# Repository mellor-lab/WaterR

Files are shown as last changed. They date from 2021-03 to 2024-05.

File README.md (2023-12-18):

# WaterR

WaterR is an open-source device developed in the Dodson lab at the University of Bristol to automate fluid restriction in experimental rodents. It allows the user to: set water-availability time windows, set a maximum daily volume allowance, or deliver ad libitum water to assess baseline water consumption. Automating water access-control offers the opportunity to significantly refine current practice. The ability to monitor water consumption on a cage-by-cage basis and the flexibility offered in programming different water-access regimens allows the implementation of tailored restriction approaches, while at the same time offering a standardised platform to aid reproducibility across different laboratories. 
<p align="center">
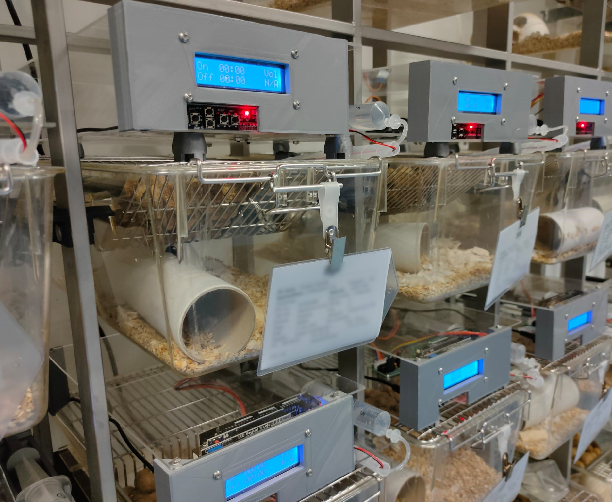
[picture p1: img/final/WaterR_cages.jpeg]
    
</p>
&nbsp;

## List of components
In the table below there is a list of all components necessary to assemble WaterR. A source for each component is added for ease but every component is readily available from other sources as well. Links or part numbers are added for ease; part numbers are provided as manufacturer numbers instead of supplier as it makes it easier to source the items from a different supplier should you need to do so. Multi-buy options are provided when possible as they are cheaper, the quantity required for a single WaterR unit is listed in the table.  
Note: it is important that the power supply is a grounded, desktop power supply (i.e. a "brick") with a low ripple current (<100 mV peak-to-peak), otherwise it could interfere with the signal from the piezoelectric vibration sensor. These can be quite expensive (£40-50 each) but they provide up to 6-8 Amps, and as 1 WaterR unit uses ~500 mA you can safely power multiple units from one supply. Refrain from using a cheap switching power supply!

| Component                         | Source            | Catalog num / reference | Q.ty for 1 unit    |
|-----------------------------------|-------------------|-------------------------|--------------------|
| **Main items**                    |                   |                         |                    |
| ELEGOO Mega 2560                  | Amazon            | https://amzn.to/380VEm9 | 1                  |
| LCD keypad shield                 | Amazon            | https://amzn.to/3uISKfw | 1                  |
| Data Logging shield with RTC      | Amazon            | https://amzn.to/3ra0zZz | 1                  |
| Stepper Motor 28byj-48, 5V, 1:64  | Amazon            | https://amzn.to/2NCnqOH | 1                  |
| A4 acrylic sheet, 2mm             | Amazon            | https://amzn.to/2Ps0bYr | 2                  |
| Terumo 20ml syringe               | Medline Scientific| BS-20ES                 | 1                  |
| **Spout block**                   |                   |                         |                    |
| Piezoelectric sensor              | RS components     | 285-784                 | 1                  |
| Hook up wire, red                 | RS components     | 872-4460                | 30 cm              |
| Hook up wire, black               | RS components     | 872-4458                | 30 cm              |
| Resistor, 10 MΩ                   | Farnell           | RE03841                 | 1                  |
| Heath-shrink tubing               | Amazon            | https://amzn.to/3uOrmwP | various sizes      |
| 2.54 mm pin header , 2x1          | RS components     | 251-8086                | 1                  |
| Spiral Wrap                       | RS components     | 227-980                 | 15 cm              |
| Fitting, female luer to 1/16 barb | Cole-Parmer       | 45508-00                | 1                  |
| Fitting, male luer to 1/16 barb   | Cole-Parmer       | 45505-22                | 1                  |
| Tygon tubing, 1.6 ID x 3.2mm OD   | Cole-Parmer       | ACF00002                | 20 cm              |
| Surflo cathether 16Gx51mm         | VWR International | SR+OX1651C1             | 1                  |
| **Power**                         |                   |                         |                    |
| DC power splitter, 5 way          | Farnell           | C-PS-5W                 | 1 shared among 5   |
| DC power extensions, 1M           | Farnell           | PSG02089                | 1                  |
| Power supply, 9V, 4.5A            | RS components     | 175-9086                | 1 shared among 6-8 |
| **Fasteners**                     |                   |                         |                    |
| Screw, M3 x 20mm                  | Technobots        | 4304-320                | 4                  |
| Screw, M3 x 8mm                   | Technobots        | 4304-308                | 2                  |
| Screw, M3 x 6mm                   | Technobots        | 4304-306                | 14                 |
| Screw, M3 x 8mm, countersunk      | Technobots        | 4304-408                | 2                  |
| Nut, M3                           | Technobots        | 4310-025                | 6                  |
| Zip ties, 250mm	            | Amazon            | https://amz.run/5GKi    | 1                  |
| Dupont wires, 10cm                | Amazon            | https://amzn.to/3834WxT | 6 (f-m), 1 (m-m)   |
| CR1225 lithium battery            | Farnell           | CR1225                  | 1 (or 0)           |

## Tools
M3 Hex screwdriver (2mm)  
M3 Hex nut driver (5.5mm)  
Electric drill (4mm drill bit)  
Dremel  
Soldering iron  
Wire cutter

## 3D printed parts
You should print all the files in the /stl_parts folder. FDM printers are better suited for this job as it doesn’t require laser precision and it’s faster. Everything except for the Pump_motor_pinion.stl and the Spout_cover.stl can be printed at 0.15mm layer size, the former should be printed at least at 0.1mm or 0.06mm. Pump_rack should be printed sideways to avoid having weak line spots at the top of the teeth.

## Controller block
Take the keypad shield and cut the pin that would connect to pin 10 of the Arduino as shown in figure (this is to avoid conflicts with the clock/sd shield). 
<p align="center">
    
</p>
&nbsp; 

Take a male-male dupont cable and cut it in half. Solder the cut extremities onto the clock/sd shield, in the holes labelled SDA and SCL on the board (as shown in image). Sometimes the shield comes with 2.54 mm header soldered in this position, in this case just solder the wires to the corresponding header pins.
Add the CR1225 button battery in the clock/sd shield if it came without one. If it came with one you can still swap in a fresh one as these shields can sit on a shelf for years, affecting the amount of charge left in the battery.
<p align="center">
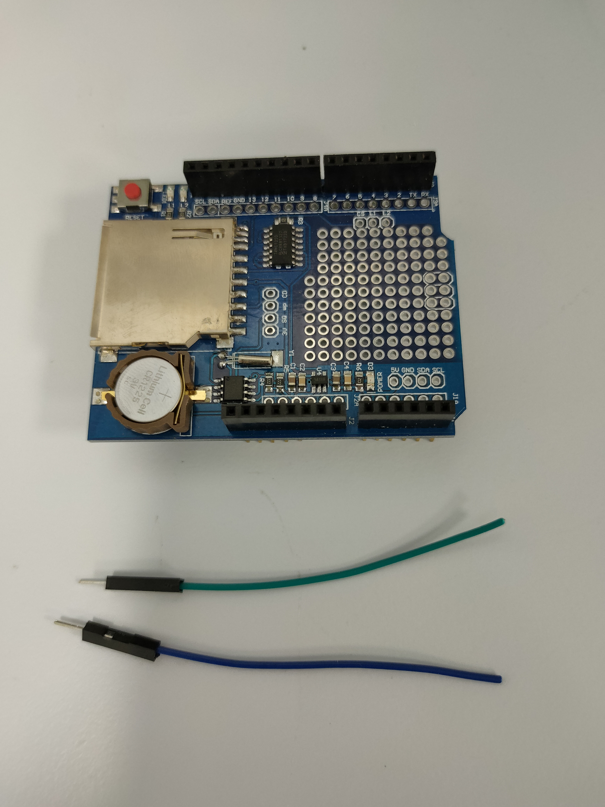
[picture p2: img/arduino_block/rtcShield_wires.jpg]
    
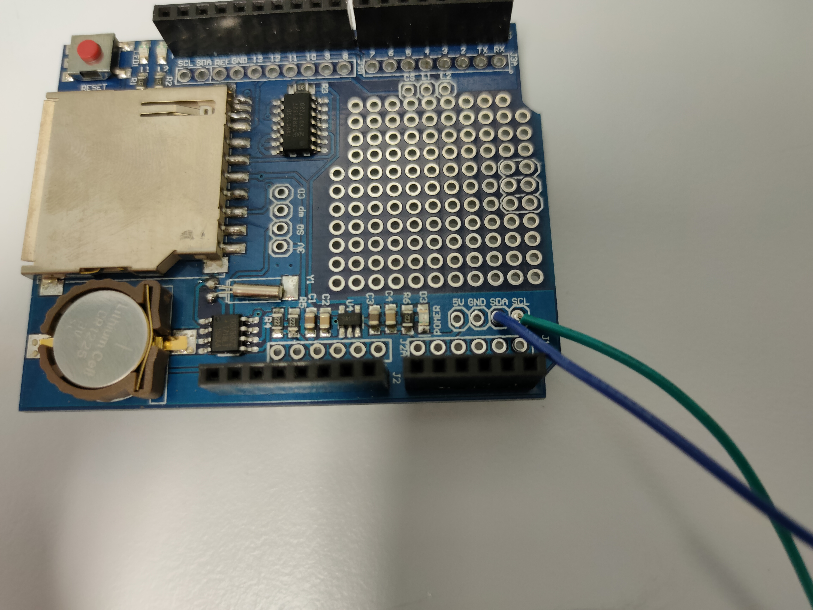
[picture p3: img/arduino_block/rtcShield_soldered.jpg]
    
</p>
&nbsp;

Slot the clock/sd shield onto the Arduino and connect the SDA wire on the SDA pin (pin 20) on the Arduino and do the same with clock/sd shield SCL and Arduino SCL (pin 21). Slot the LCD keypad shield on top of the clock/sd shield.
<p align="center">
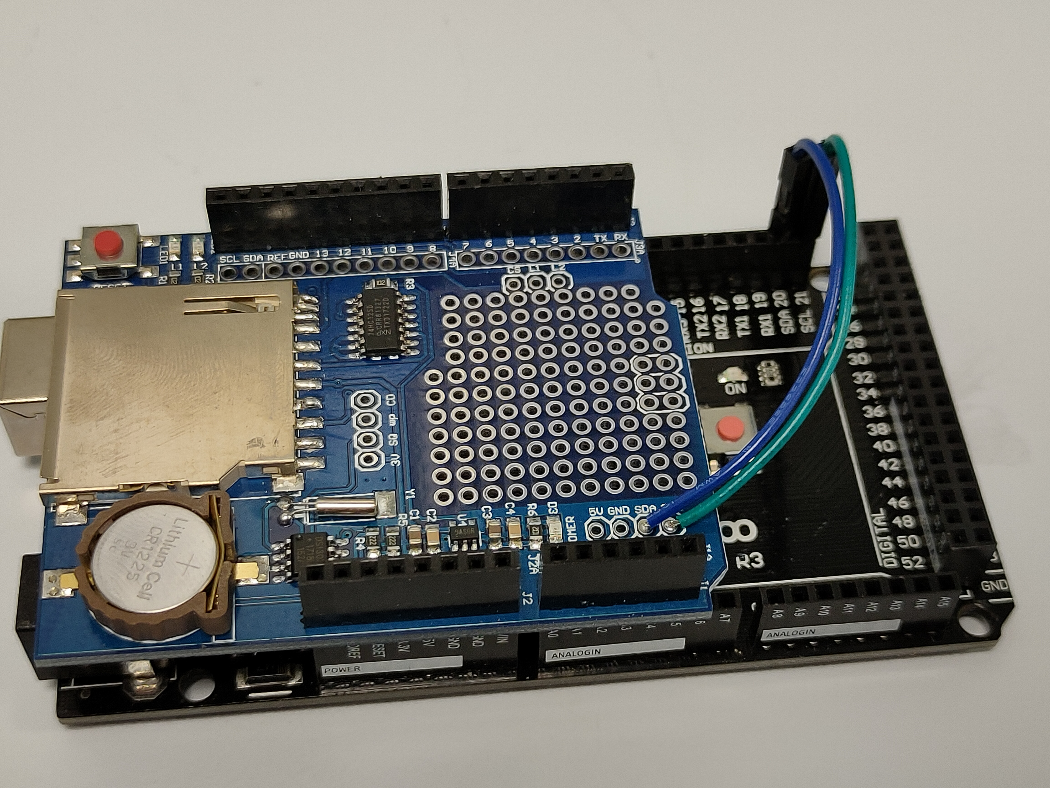
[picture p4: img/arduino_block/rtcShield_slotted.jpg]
    
</p>
&nbsp;

Now we can upload the software required to sync the clock and the WaterR firmware.

## Software
1. Install the [Arduino IDE](https://www.arduino.cc/en/software) if you have not done so already.

2. Download the WaterR repository to your computer.

3. Download the contents of the /libraries folder and paste them in your user/documents/Arduino/libraries folder. 

4. Connect the Arduino to your PC through USB. Run the IDE and make sure you select Tools -> Board -> Arduino Mega or Mega 2560. Also, in Tools -> Port select the COM port assigned to your Arduino.

5. In the /Arduino_sketches folder there are 3 sketches that should be uploaded to the Arduino. Open and Upload one after the other in the following order:

> Before uploading the sync_clock sketch, open the Serial Monitor. Set the baud rate to 9600.
- Upload **Sync_clock**.  
This sketch synchronizes the DS1307 clock chip on the Arduino RTC shield with the clock on your PC. If everything is wired correctly and the sketch successfully uploads, you should see the Arduino outputting date and time to the serial monitor. Now close the serial monitor. Make sure not to restart the Arduino (do not disconnect, reset, nor open the Serial Monitor) as this could introduce clock discrepancies.
- Upload **Load_defaults**.  
This sketch loads some default values in the Arduino EEPROM.
- Upload **WaterR_main**.  
This sketch is the main WaterR firmware. If you cannot read any character on the lcd screen, you should adjust the contrast by turning the screw on the blue potentiometer clockwise until you can comfortably see white characters. 
6. You can safely disconnect the Arduino from the PC. WaterR is thought as a stand-alone device so after this sketch is uploaded it should not be necessary to reconnect it to a PC unless you want to modify the main program, in which case you will need to re-upload the modified version.
<p align="center">
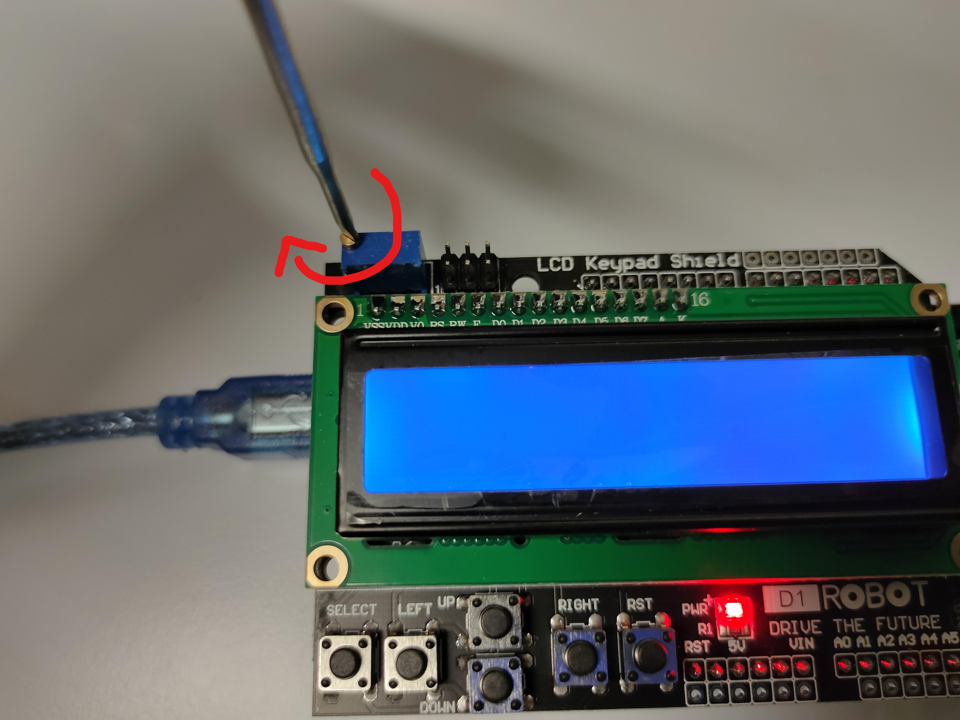
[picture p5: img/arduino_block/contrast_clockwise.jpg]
    
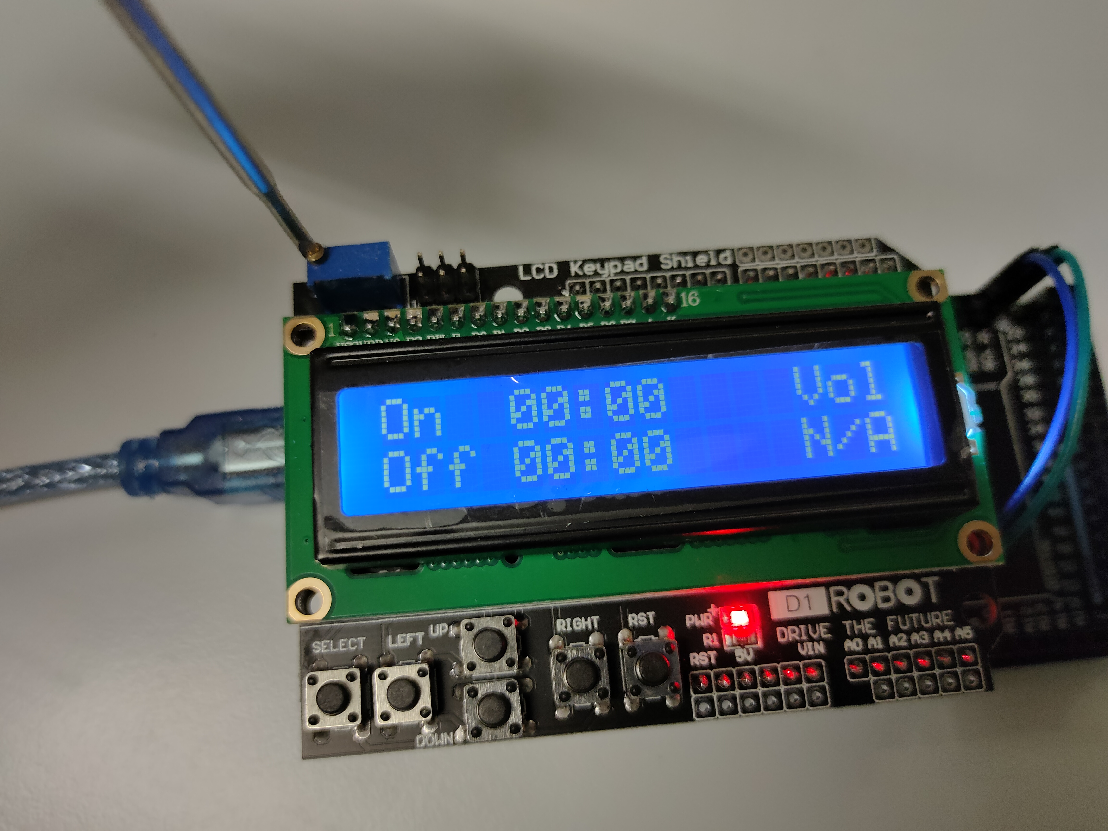
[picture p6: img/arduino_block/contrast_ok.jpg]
    
</p>

## Spout block
Remove the intravenous catheter from the packaging. Remove the plastic sleeve and the luer cap/filter. Cut it so that the metal cannula is 4 cm long. Best way of cutting it is making an incision with a dremel and then use pliers to snap it. Blunt the edge.
<p align="center">
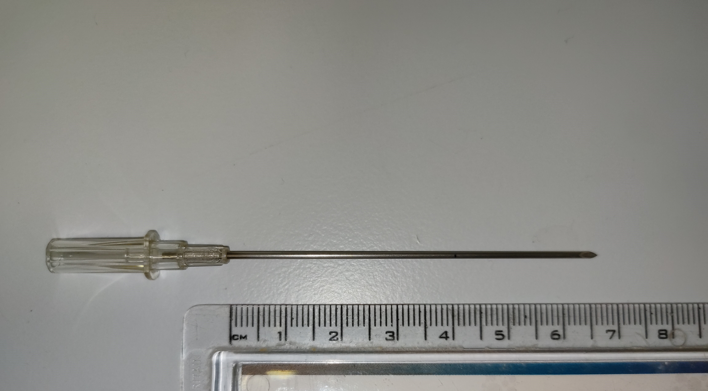
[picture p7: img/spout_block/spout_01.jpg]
    
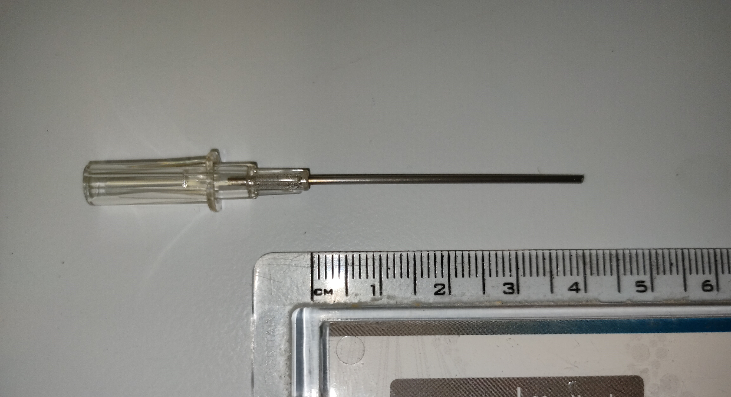
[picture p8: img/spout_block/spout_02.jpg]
    
</p>
&nbsp;

Slide a piece of 2.4mm heat-shrink tubing (enough to completely cover the piezoelectric sensor) on the metal end up to the proximal end.
Insert the piezo element between the heat shrink tubing and the metal cannula, with the 2 leads toward the female luer end. Apply heat to shrink the tubing, securing the piezo element.
<p align="center">
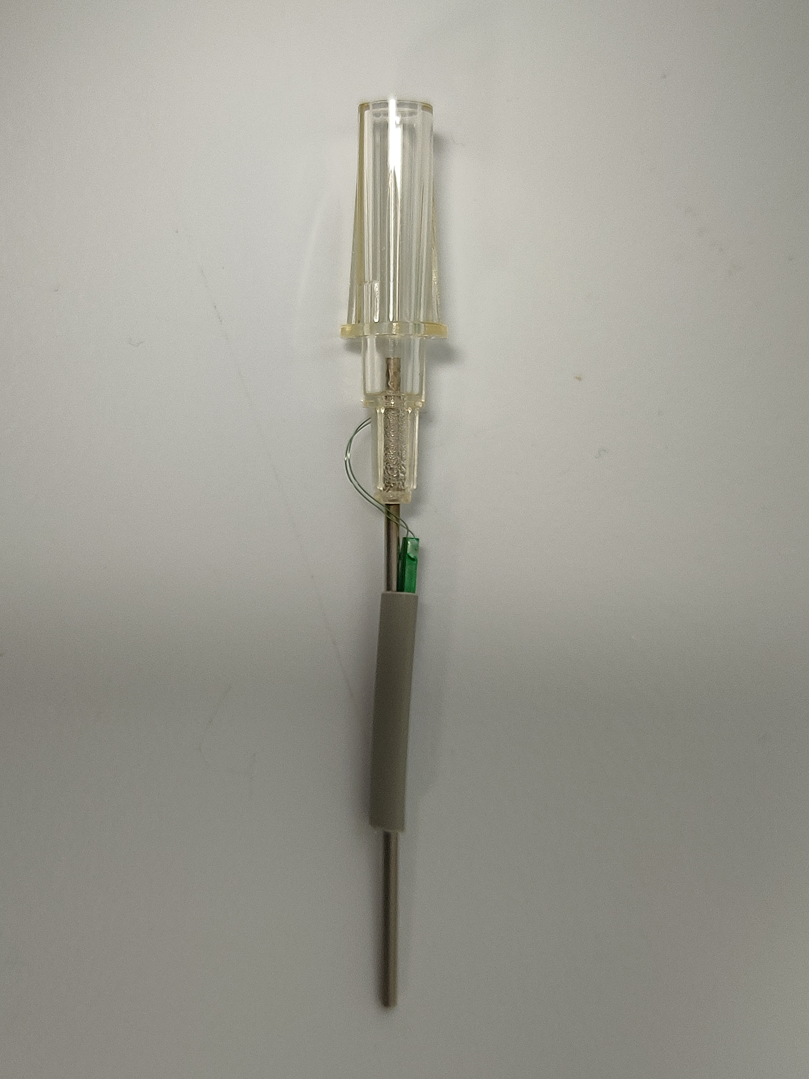
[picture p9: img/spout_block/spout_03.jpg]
    
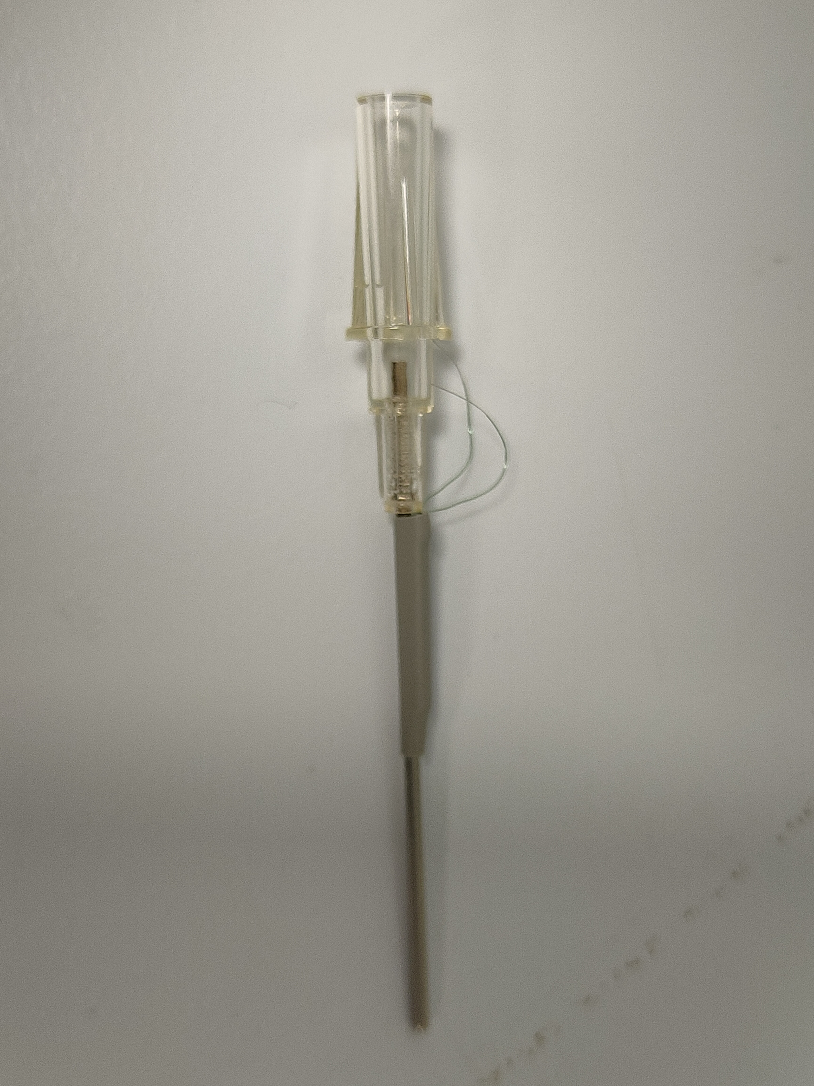
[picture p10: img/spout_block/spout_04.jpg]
    
</p>
&nbsp;

Solder the 2 leads to 2 lengths of wire (30 cm).
<p align="center">
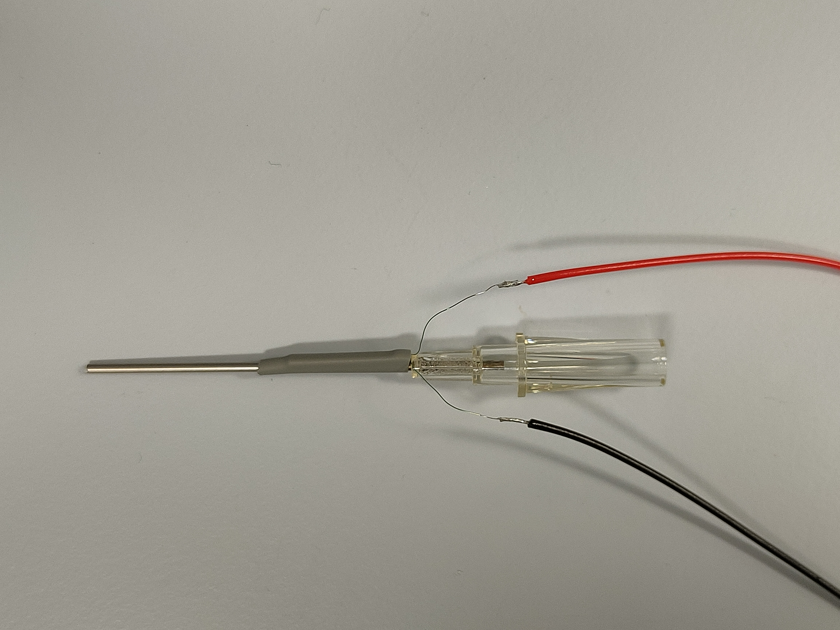
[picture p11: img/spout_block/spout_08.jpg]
    
</p>
&nbsp;

Slide 1 pieces of 3.2mm heat shrink tubing (blue in the image) and a 6.4mm one (yellow) on the plastic part of the spout. Shrink it to secure the wires in place. Make sure that the leads of the piezo element are a bit loose and not too much in traction.
<p align="center">
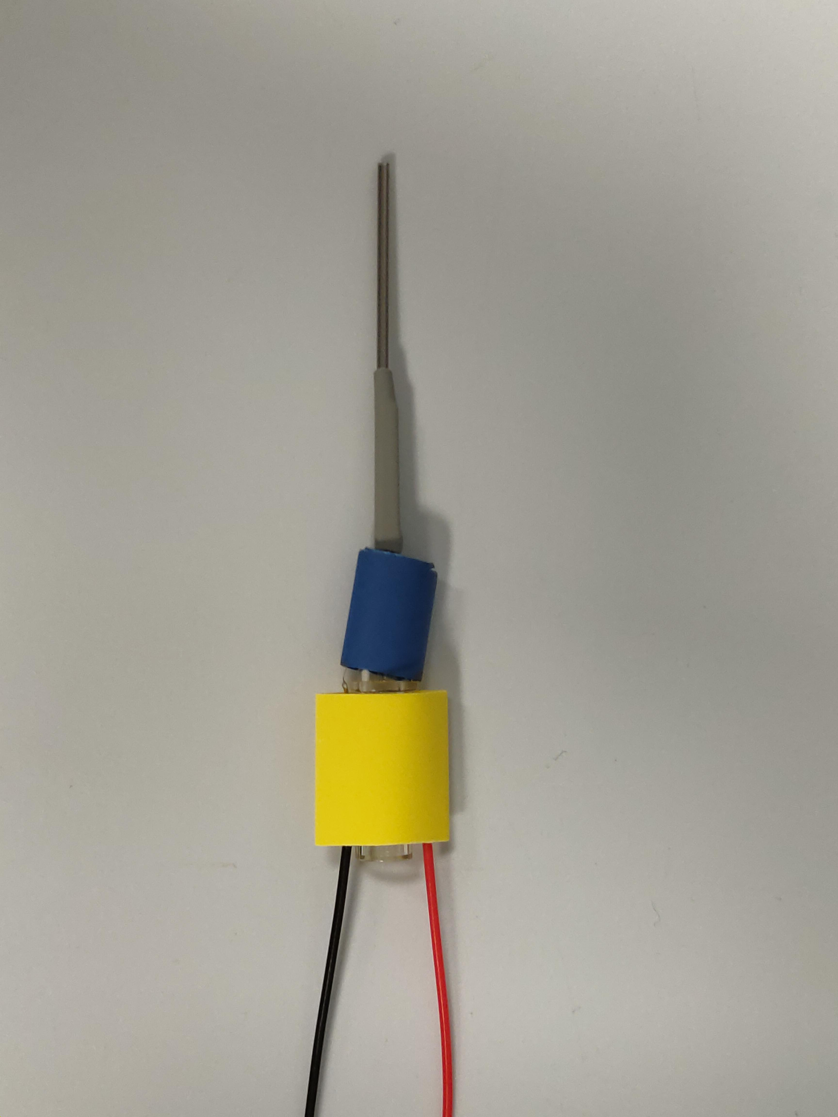
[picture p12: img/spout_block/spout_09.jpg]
    
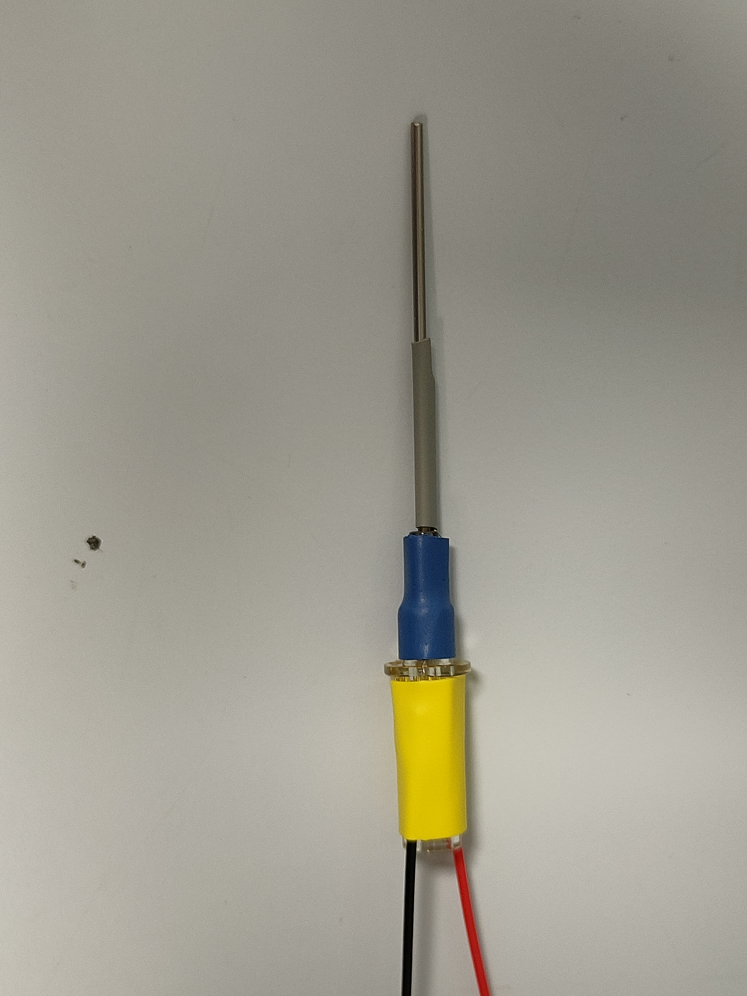
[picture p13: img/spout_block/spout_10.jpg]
    
</p>
&nbsp;

Strip the distal end of the wires as shown in the picture. Solder a 10 MΩ resistor at the wire junctions (so that it is wired in parallel to the piezo element) and a 2x1 header pin at the terminals. Cover the solder joints with heat shrink tubing. You can use small pieces of heat shrink tubing to keep the wires together and tidy.
<p align="center">
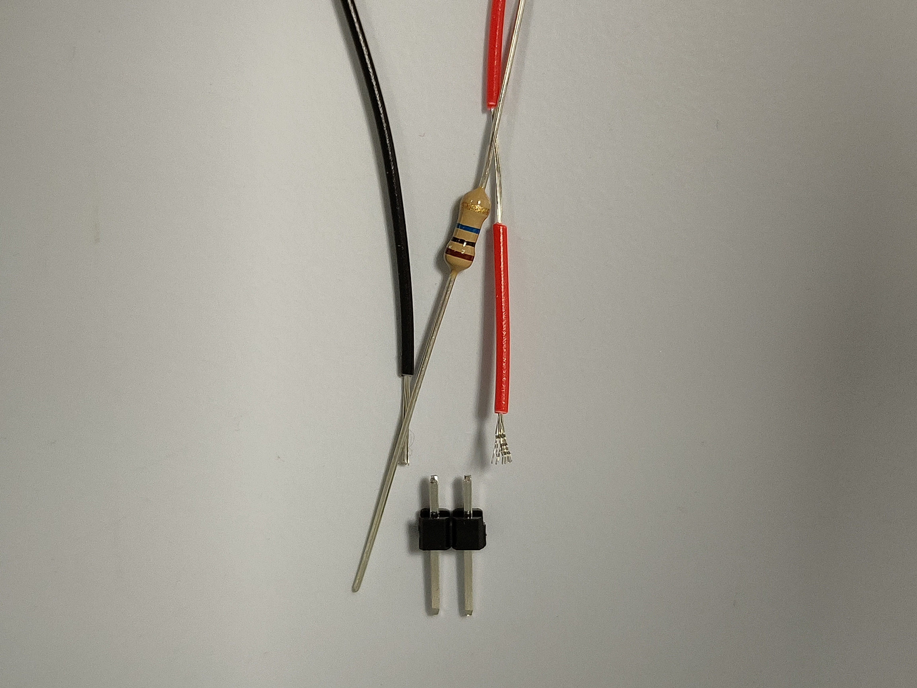
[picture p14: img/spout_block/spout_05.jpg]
    
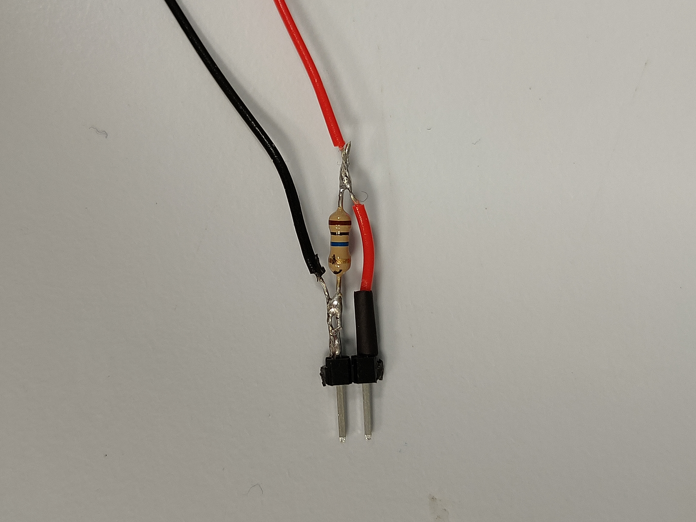
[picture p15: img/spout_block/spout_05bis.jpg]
    
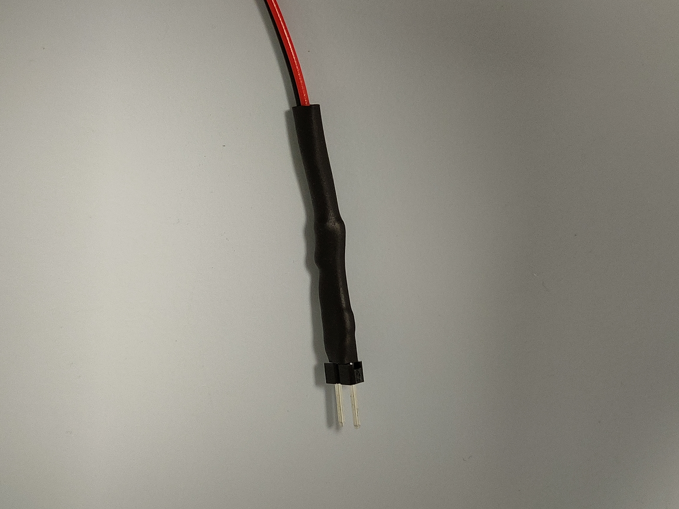
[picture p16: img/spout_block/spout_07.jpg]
    
</p>
&nbsp;

Take 20 cm of tubing and connect it to the barbed end of both the male and female luer fitting.
Carefully thread the spout into the 3D printed hook support. Fix it in place using the male luer fitting, then screw the 3D printed cylinder into the thread to protect the piezo element (carefully not to damage the piezo element leads). Make sure the piezo is parallel to the ground (i.e. fully on top or fully below the spout) to maximize sensitivity.
Wrap both the tubing and the wires in the wire protector spiral (15 cm).
<p align="center">
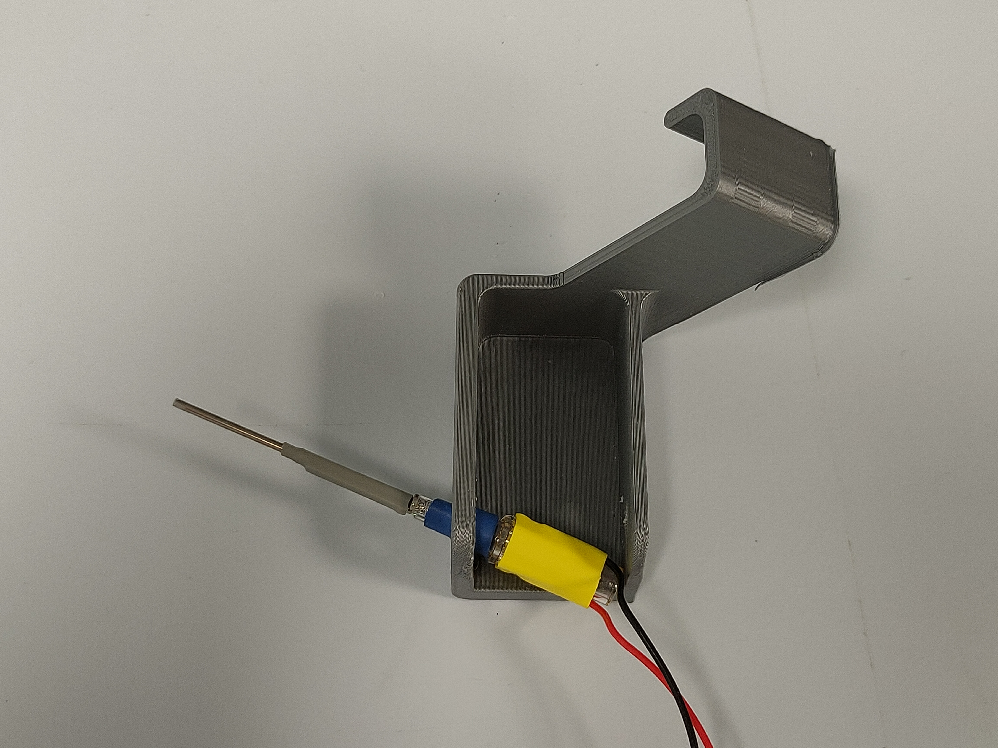
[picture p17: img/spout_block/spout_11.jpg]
    
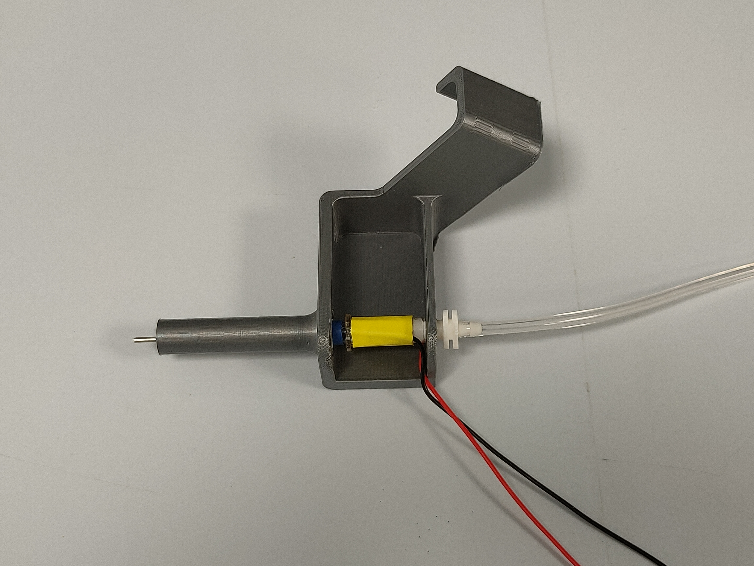
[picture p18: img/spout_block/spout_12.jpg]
    
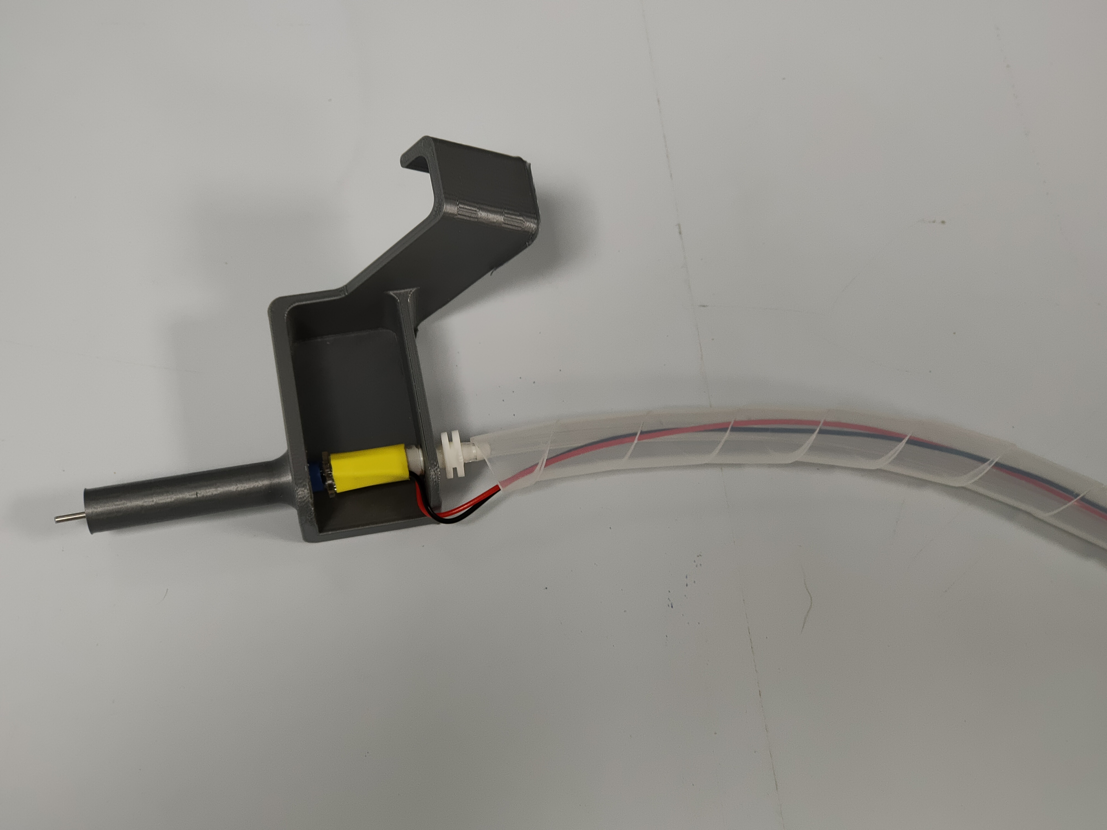
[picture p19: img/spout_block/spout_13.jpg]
    
</p>

## Pump block
Put the rack into its slot and make sure it slides freely with no resistance.
Slot the pinion on the stepper motor shaft. It should be tightly press-fit so print it again if it is even slightly loose.
Use 2 8mm screws + nuts to secure the stepper motor in position. The easiest way of doing this is to initially not tighten the screws all the way but have them slightly loose. Push the pinion onto the rack with one finger, then align the motor so that the 2 eyelets are horizontal. Tighten the screws, making sure the pinion is making full contact with the rack.
<p align="center">
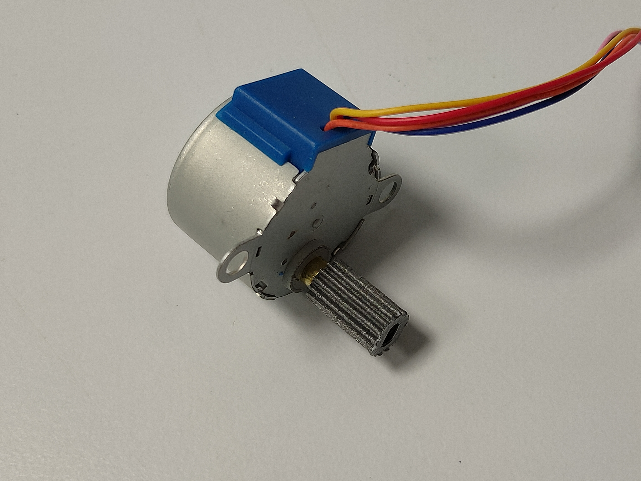
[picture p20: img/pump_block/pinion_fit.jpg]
    
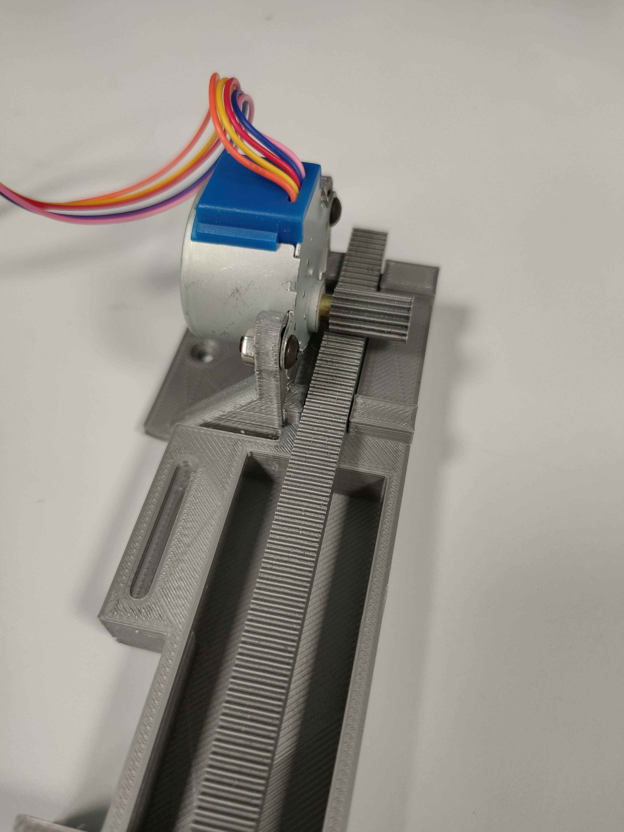
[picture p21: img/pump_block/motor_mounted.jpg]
    
</p>

## Main Assembly
Take the cage that you will be using the device with. Put the plastic feet on the top grid in the final position you want them to go. Put the first acrylic sheet on top of them and mark the position of the threaded holes of the feet.
<p align="center">
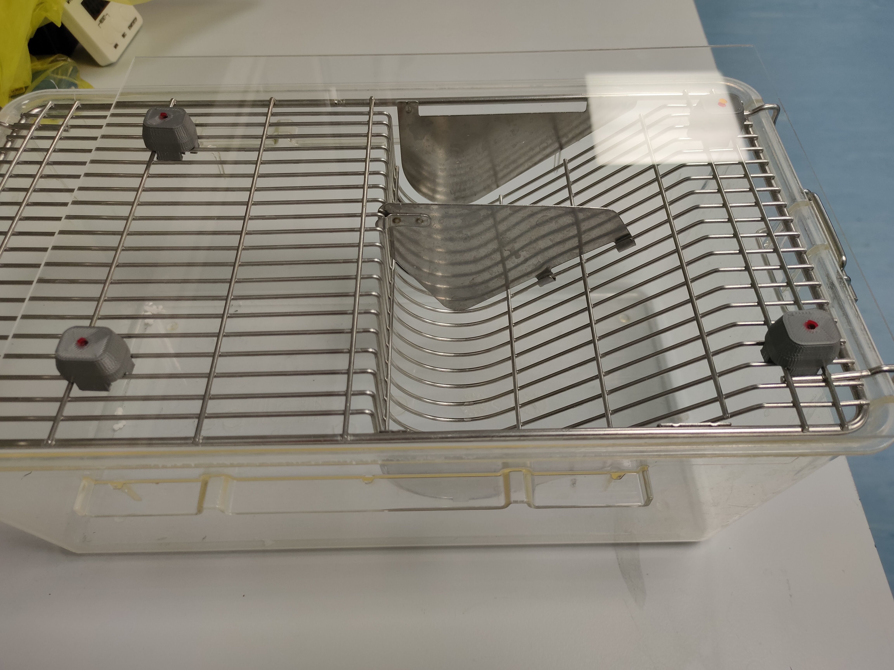
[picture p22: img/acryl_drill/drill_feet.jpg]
    
</p>
&nbsp;

Position the pump block as shown, flush with the acrylic sheet on the side of the water bottle slot in the cage. Mark the screw holes position. Make sure the pump is not obstructing the hole for the plastic foot in the same corner. Also the flat standoff should not be in the rack’s way.
<p align="center">
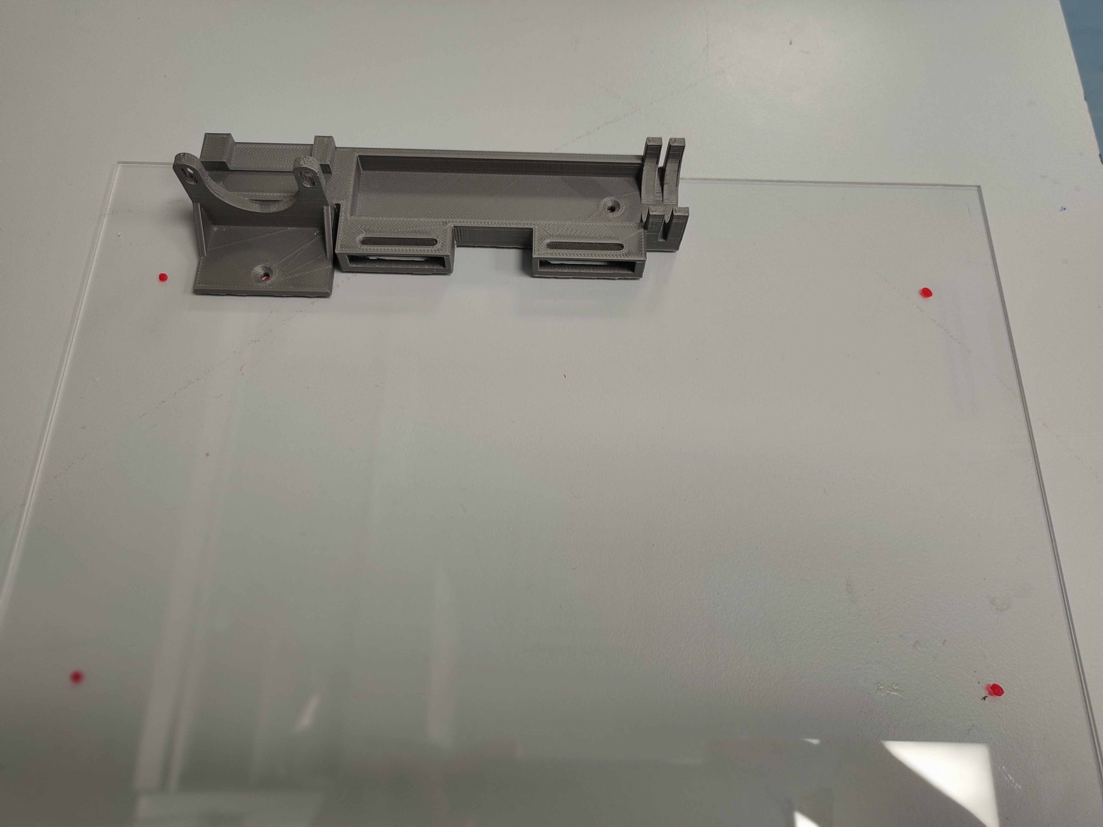
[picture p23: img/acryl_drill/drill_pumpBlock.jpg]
    
</p>
&nbsp;

Position the front panel, the corner and flat standoffs on the base acrylic sheet. Turn everything upside down (you will have to mark where to drill underneath the sheet). Mark the holes. Additionally, mark a small cutout as shown in the picture, this will make some space for when the keypad will be in place making it easier to access the buttons.
<p align="center">
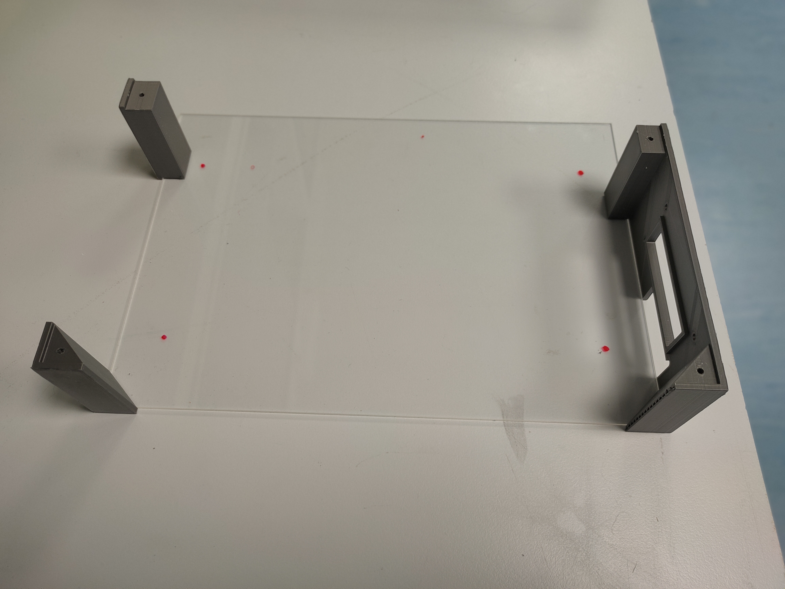
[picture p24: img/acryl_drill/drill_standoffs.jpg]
    
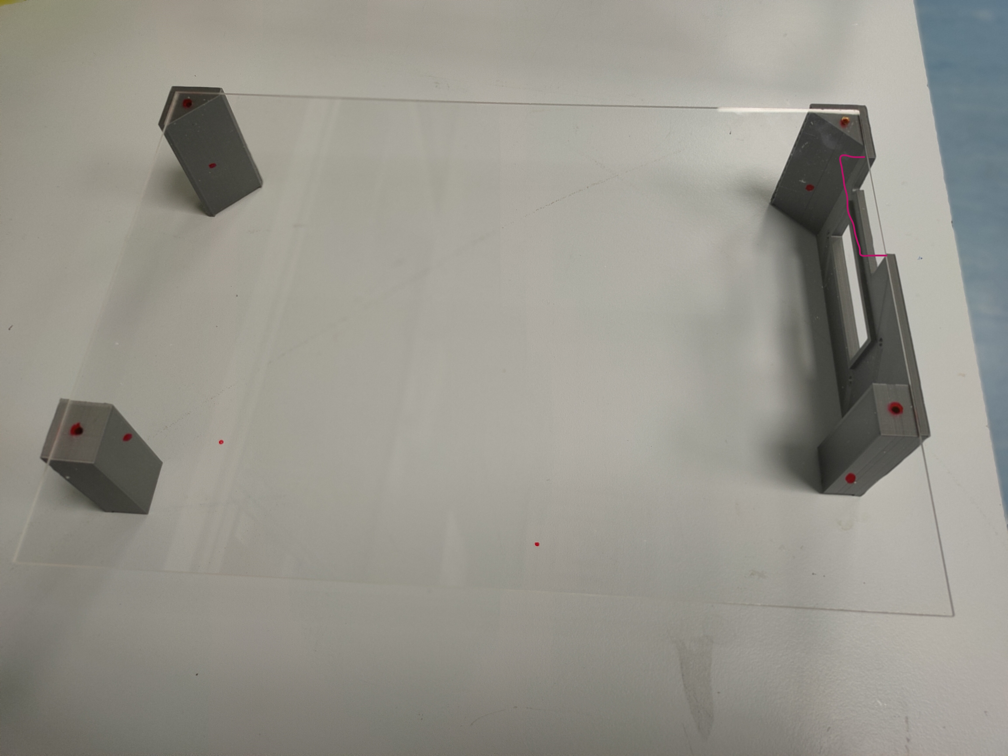
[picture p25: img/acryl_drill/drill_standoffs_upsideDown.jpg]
    
</p>
&nbsp;

Position the stepper motor driver: put the front panel and the controller block where they will end up in the final product to make sure the driver is not going to be in the way but close enough to be wired with 10cm dupont wires. Mark the holes (2 opposing corners out of 4 will be enough).
With a 4mm drill bit cut all the holes you have marked so far. Use a Dremel (a small battery one should do the job) to remove the front buttons cutout.
<p align="center">
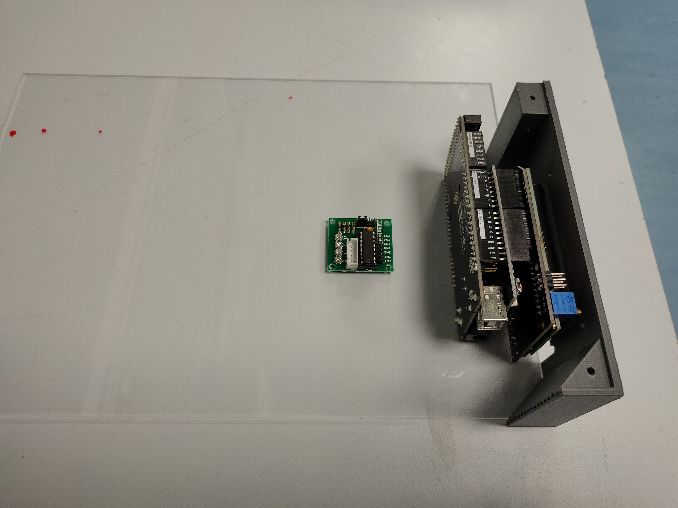
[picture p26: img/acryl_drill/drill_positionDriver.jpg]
    
</p>
&nbsp;

Mount the keypad shield on the front panel with the 20mm screws + nuts as shown. Make sure not to overtighten it, having the nuts flush with the end of the screws is enough.
<p align="center">
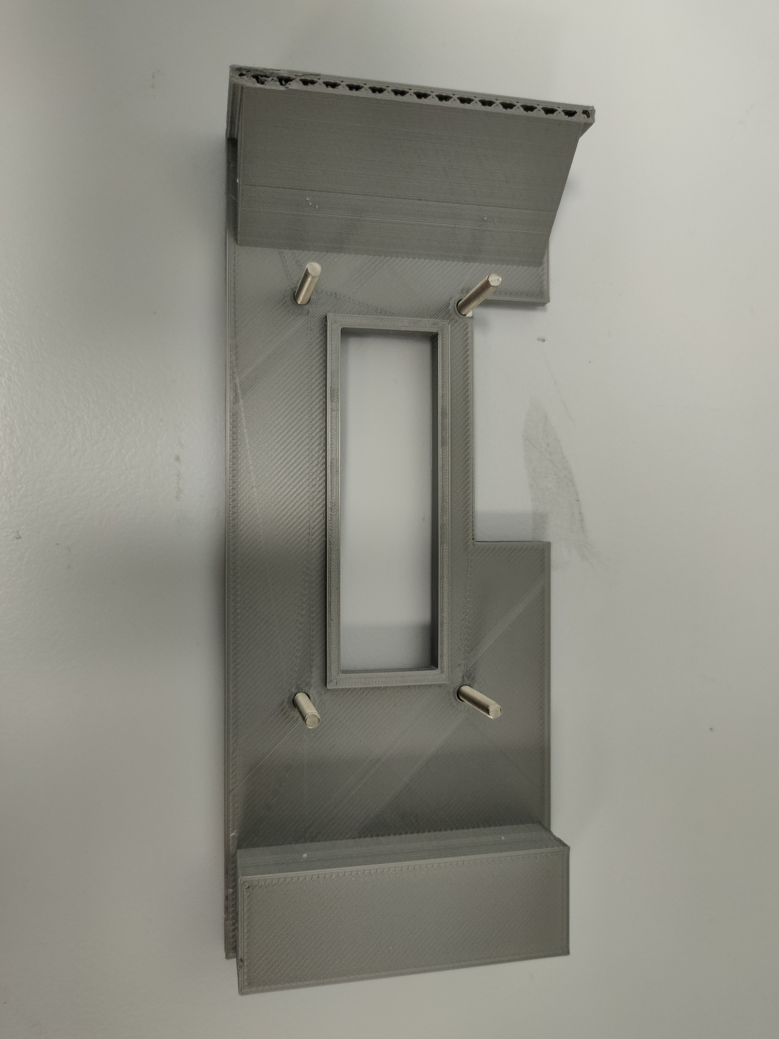
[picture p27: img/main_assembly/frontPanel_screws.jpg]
    
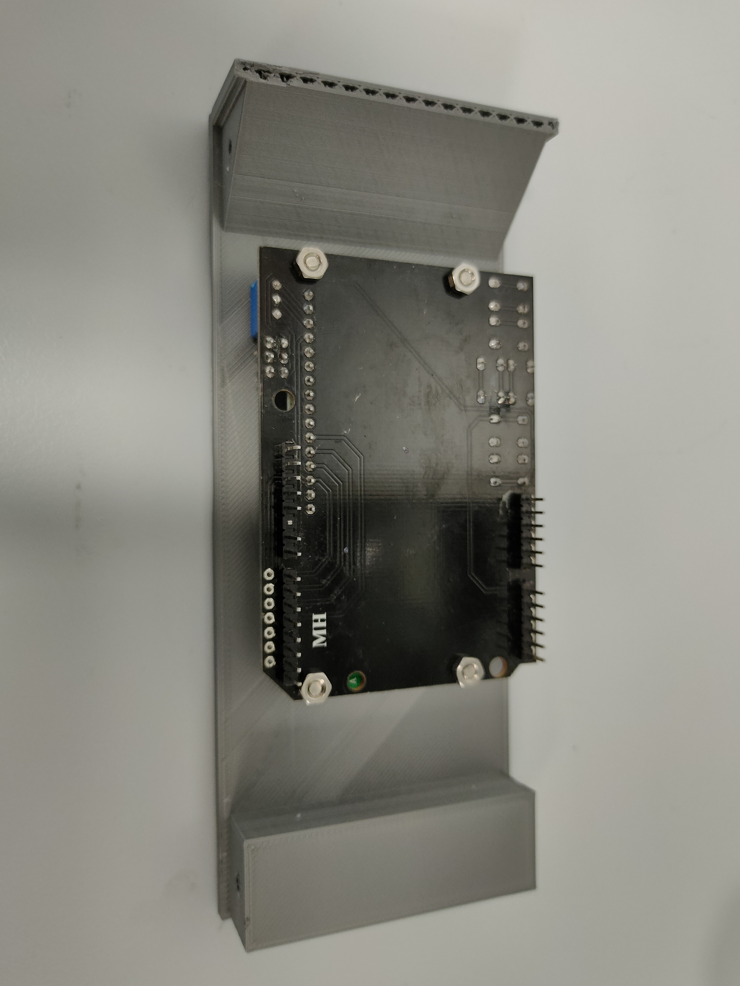
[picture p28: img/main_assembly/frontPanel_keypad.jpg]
    
</p>
&nbsp;

Screw the front panel (with the keypad shield), the standoffs and the feet on the acrylic base sheet with 6mm screws.
<p align="center">
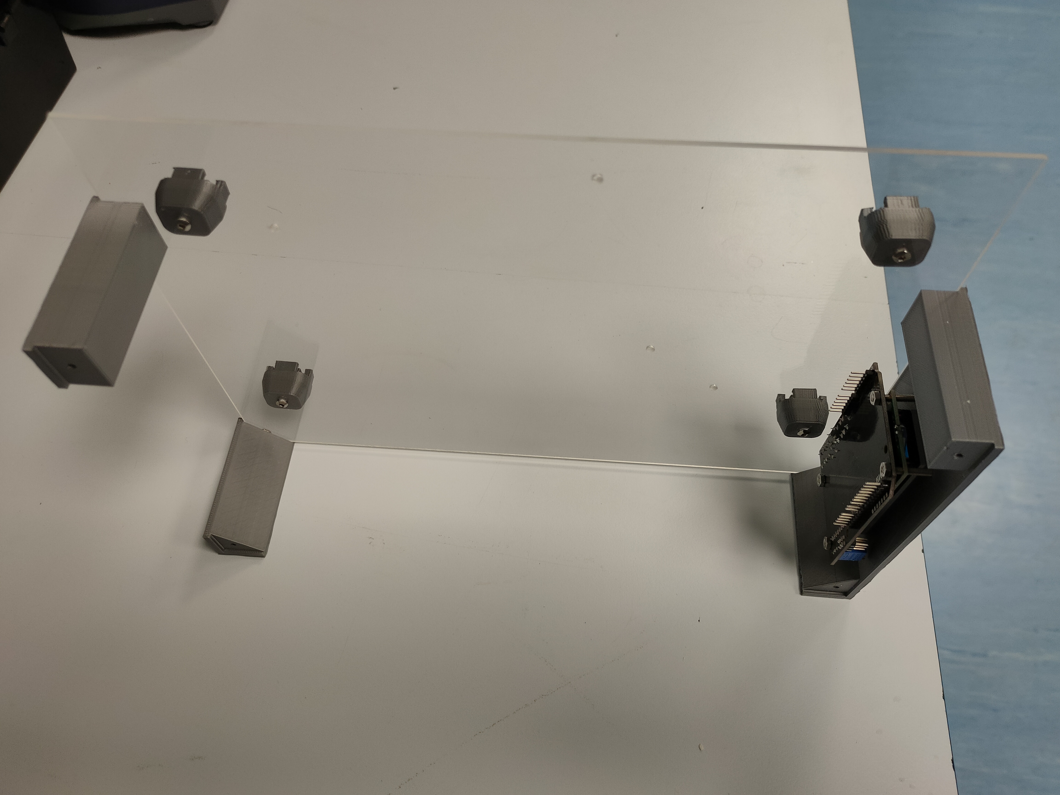
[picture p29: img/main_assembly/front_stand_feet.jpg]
    
</p>
&nbsp;

Secure the motor driver with 2 6mm screws + nuts. Screw the pump block on with 2 countersunk 8mm screws + nuts. Connect the motor’s white jst connector to the driver white receptacle.
<p align="center">
    
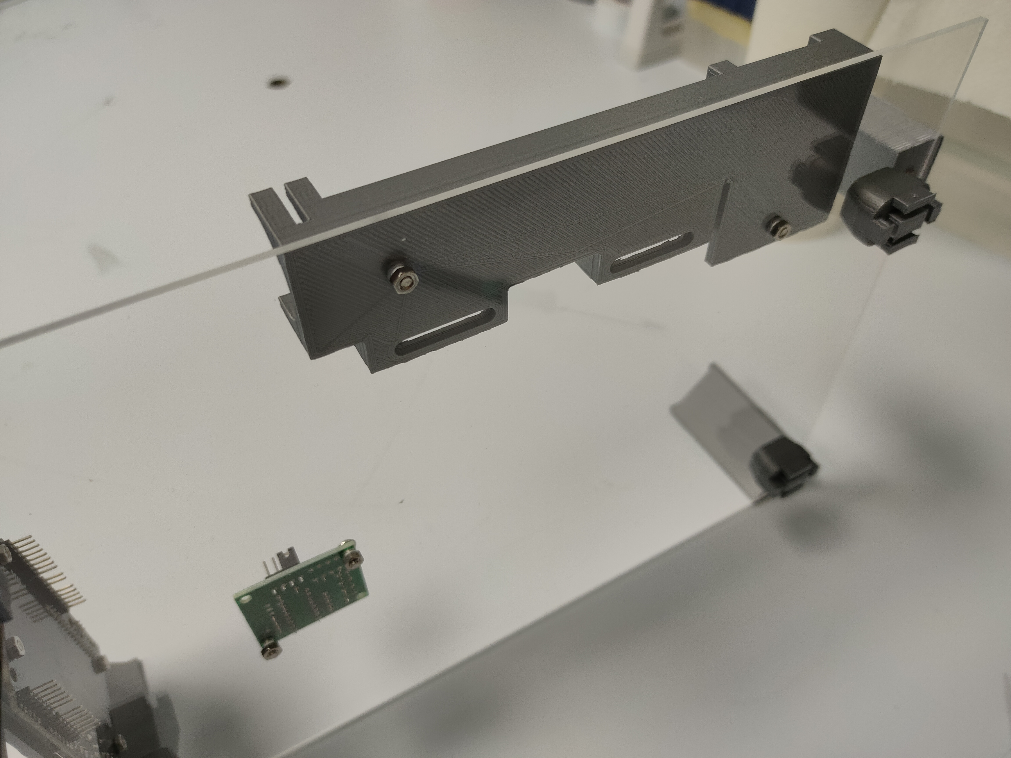
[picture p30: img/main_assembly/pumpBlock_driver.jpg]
    
</p>
&nbsp;

Use male-to-female dupont wires to connect the Arduino with the motor driver as follows:  
	Pin31 -> in1  
	Pin33 -> in2  
	Pin35 -> in3  
	Pin37 -> in4  
	5V -> 5-12V (+)  
	Gnd -> 5-12V (-)  
<p align="center">
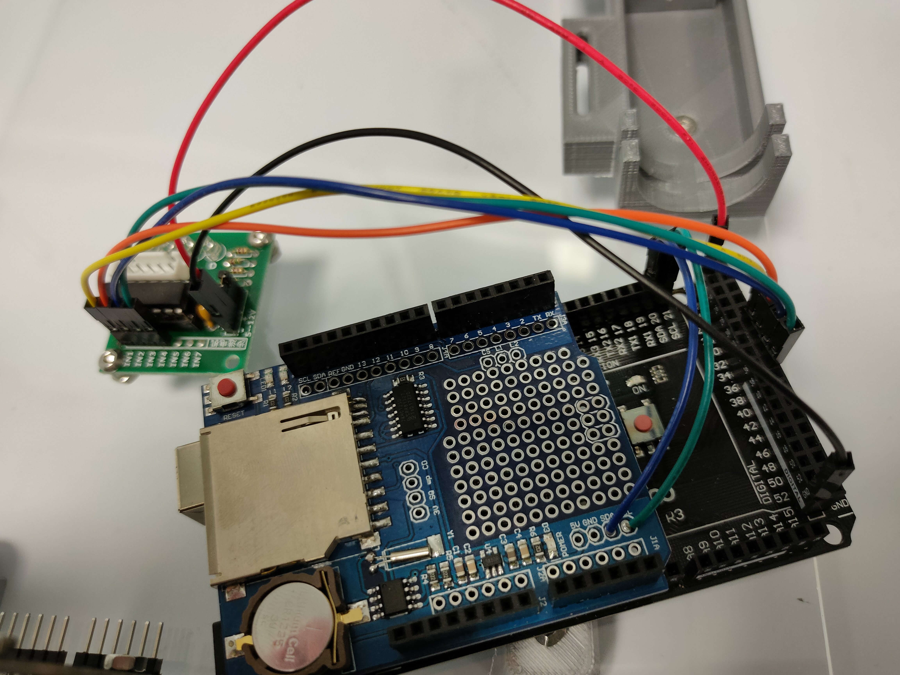
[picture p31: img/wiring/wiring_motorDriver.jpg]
    
</p>
&nbsp;

Connect the 2 pins from the spout to A8 and A9 as shown in picture (it doesn’t matter which way around).
<p align="center">
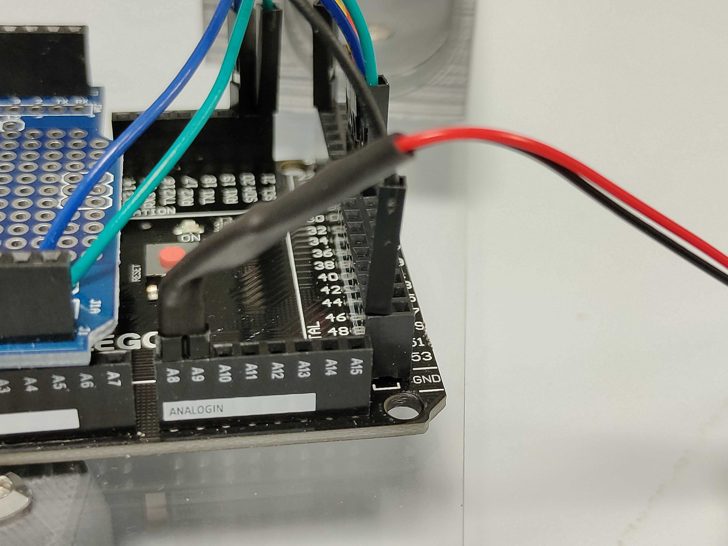
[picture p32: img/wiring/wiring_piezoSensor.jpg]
    
</p>
&nbsp;

Slot the Arduino + rtc/sd shield onto the keypad shield that is already secured to the front panel. Make sure wires are not under too much tension and make reliable contact.
<p align="center">
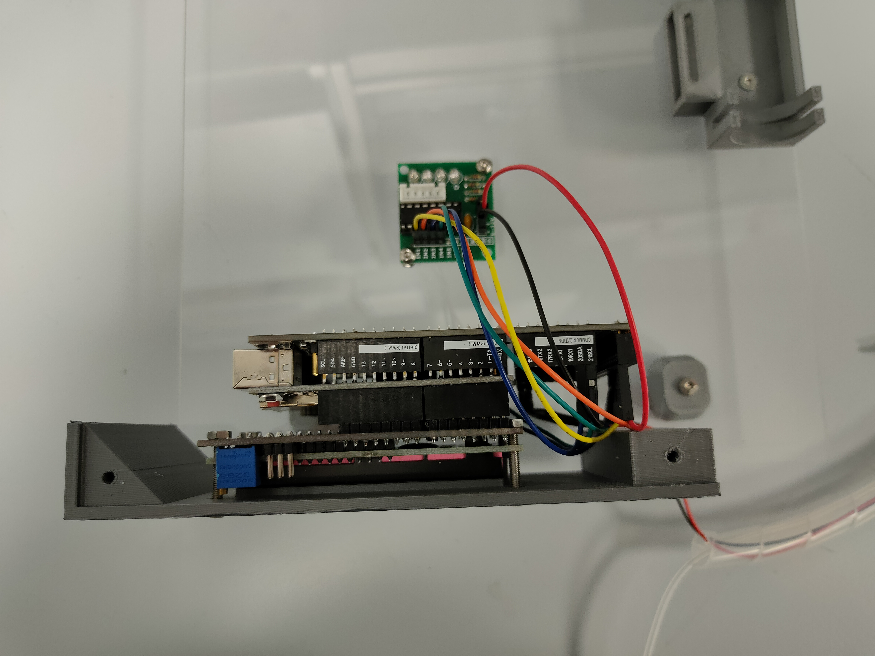
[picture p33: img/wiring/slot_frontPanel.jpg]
    
</p>
&nbsp;

To secure the front panel assembly, slide a zip tie between the pcb and the lcd screen of the keypad shield as shown in the picture and tie it. Make sure the "head" of the zip tie ends on the back of the panel and not at the bottom or top (preventing the acrylic sheets from fitting). This step is easier if you temporarily unscrew the front panel from the base acrylic sheet.
<p align="center">
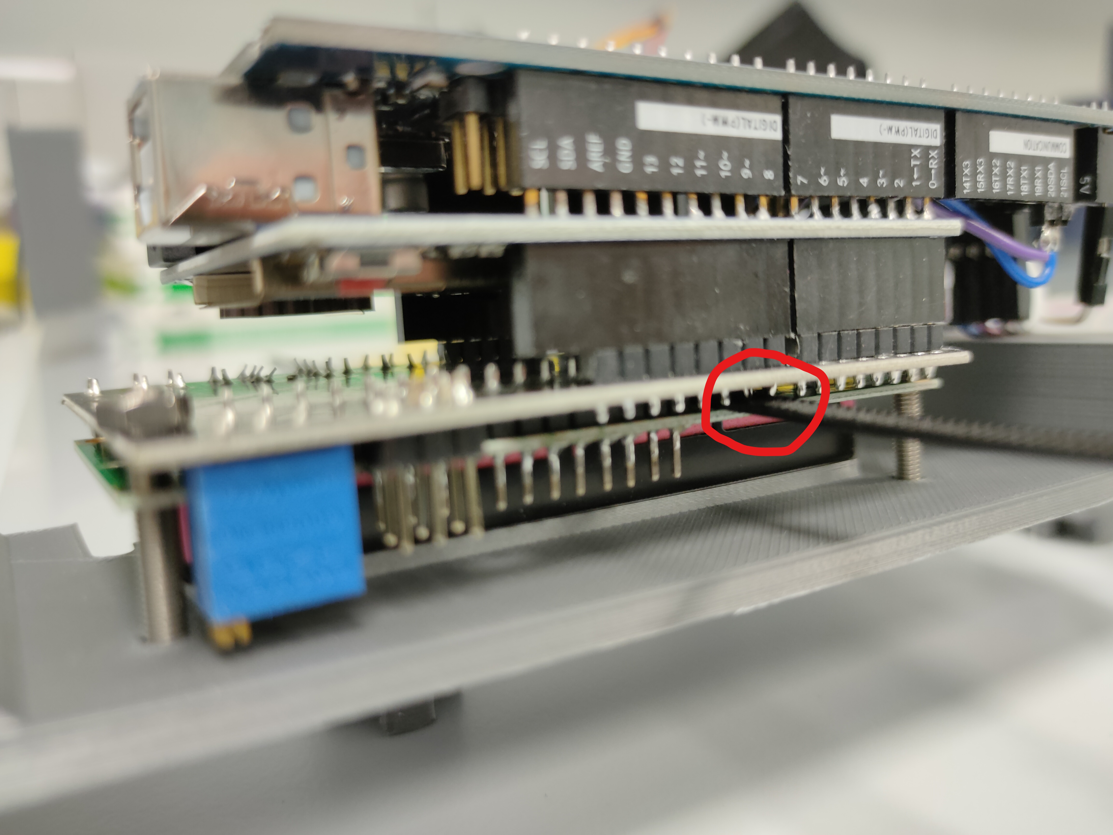
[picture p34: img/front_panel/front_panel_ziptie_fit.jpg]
    
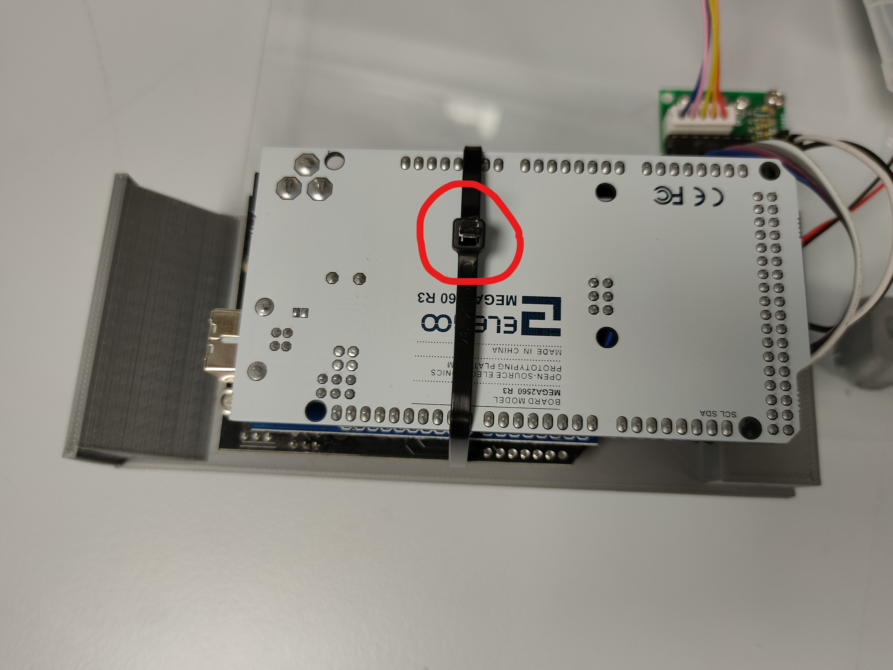
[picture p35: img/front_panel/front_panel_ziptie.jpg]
    
</p>
&nbsp;

Take the cover acrylic sheet and put it on top of the standoffs and front panel. Mark the holes. Draw a 20x4cm cutout on top of the syringe module (the resulting square should share a side with the front edge and one with the right edge of the sheet as shown in figure. Drill the holes with a 4mm drill bit and use a Dremel to remove the cutout. Secure the cover sheet with 6mm screws.
<p align="center">
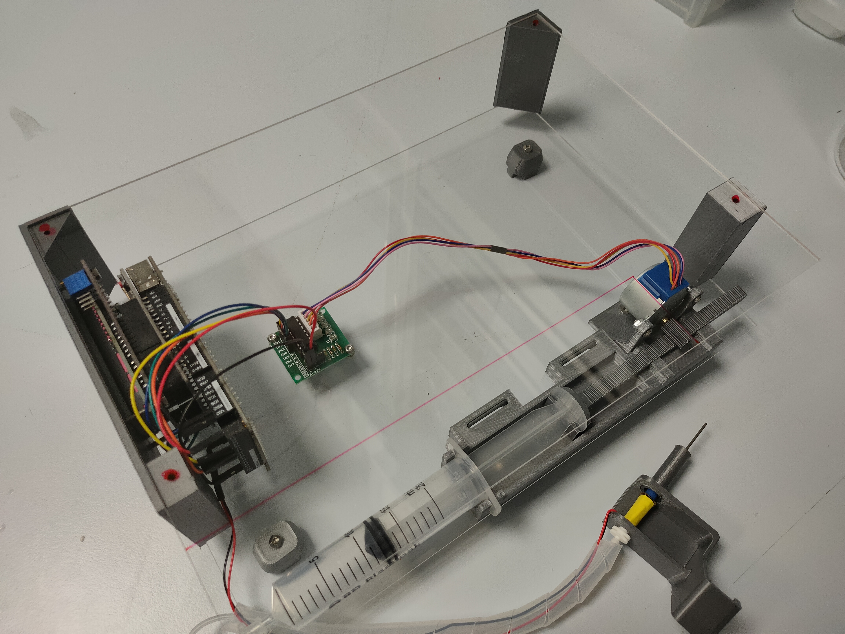
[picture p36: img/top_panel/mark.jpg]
    
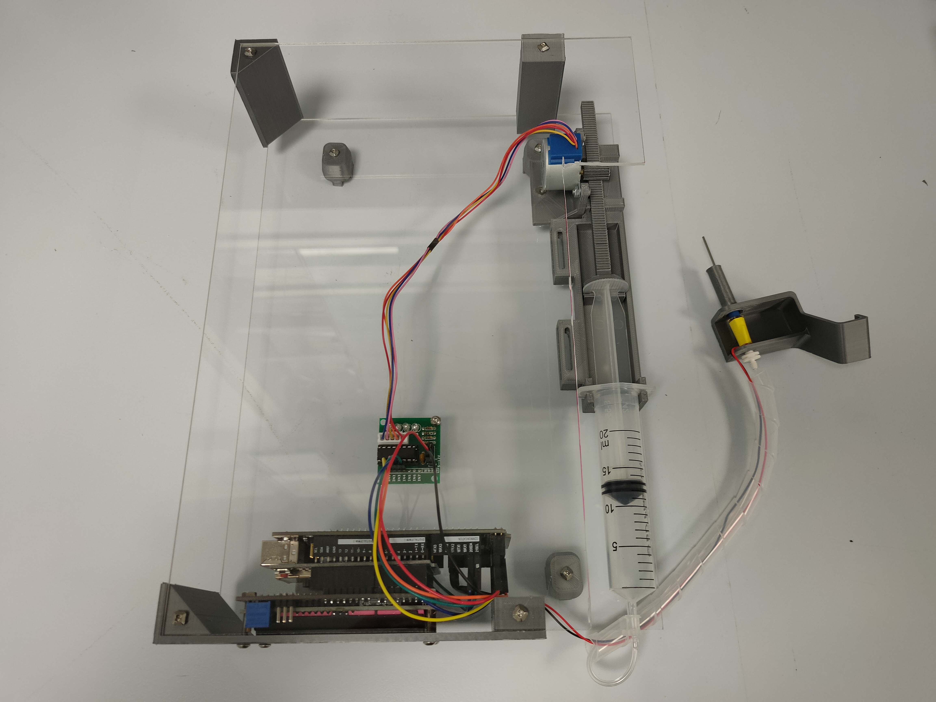
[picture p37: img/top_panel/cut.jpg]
    
</p>

## Syringe Mod
Although the pump block can fit most 20ml syringes, Terumo 20ml syringes have been giving the best results in terms of volume accuracy, as the rubber plunger seal has a very thin ridge that minimizes resistance when the motor pushes it. You can reduce resistance further by removing the back ridge by just cutting it out with a pair of scissors as shown in the pictures. This is recommended for fixed volume and monitoring use cases.
<p align="center">
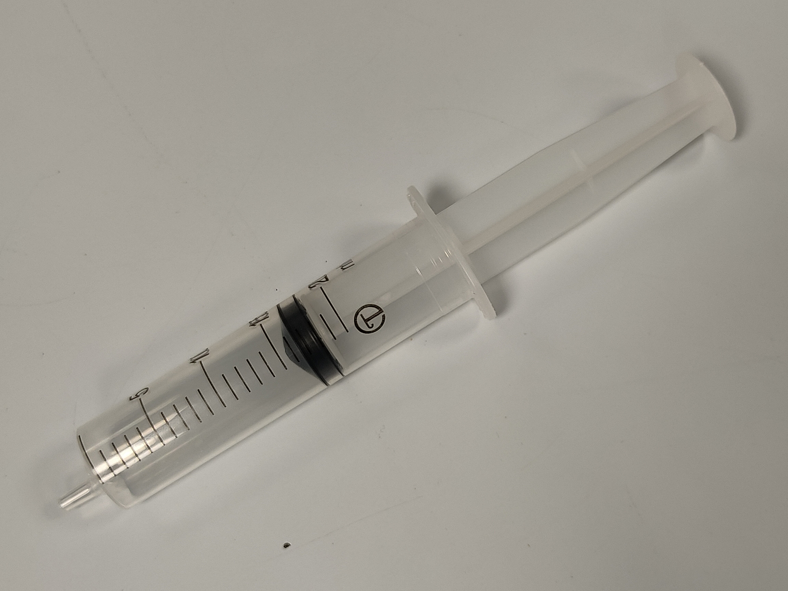
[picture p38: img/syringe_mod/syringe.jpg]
    
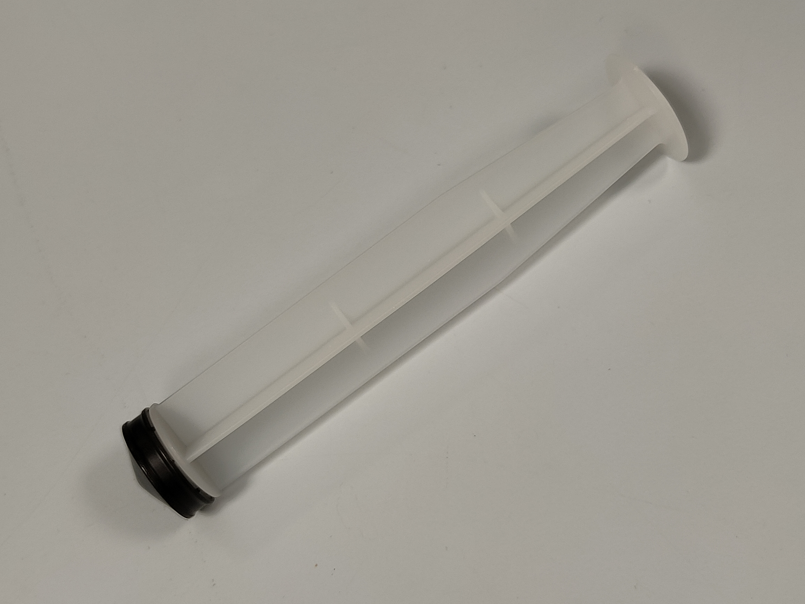
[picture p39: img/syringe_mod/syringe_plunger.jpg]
    
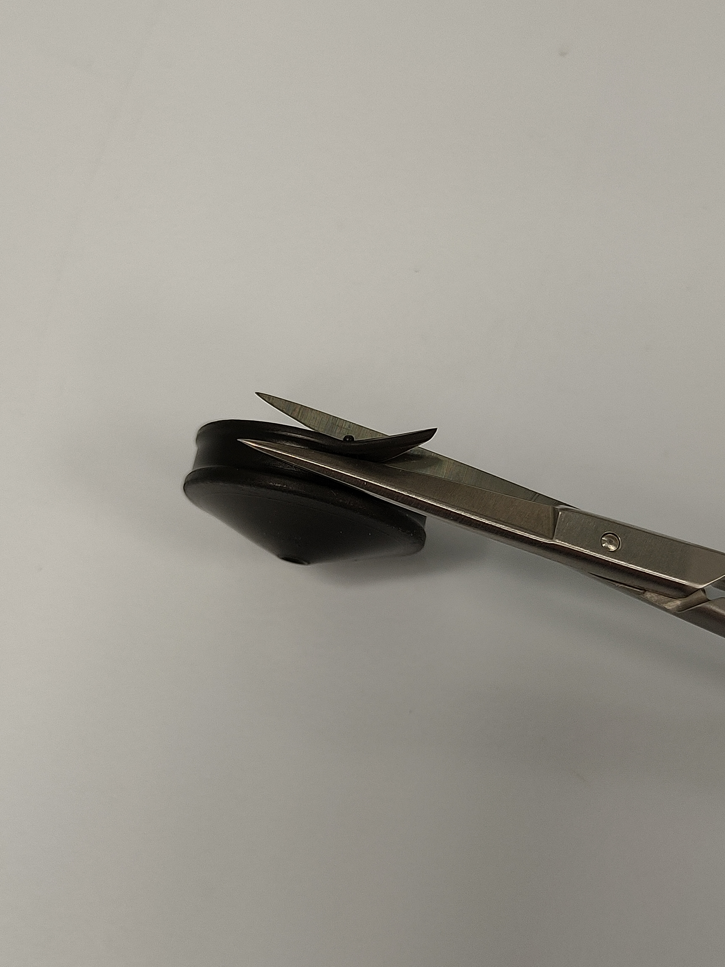
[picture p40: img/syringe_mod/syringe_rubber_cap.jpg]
    
</p>

## Final product
<p align="center">
    
    
    
</p>

## WaterR operation
WaterR default screen shows the timers that trigger availability on and off again. On the right side of this screen, the volume of the allowance is displayed (if set).
You can navigate the menus with the up/down buttons, select a sub-menu with either the right or select buttons, and go back with the left button. If no buttons are pressed for 5 seconds, the screen goes back to default. 

### Sub-menus
* **Set Timer:** this allows you to set on and off timers. The little arrow indicates the hour/minute you are currently changing. Use up/down buttons to modify, select/right to ok and step to the next one. When the off timer minutes are set and select/right is pressed, timers are saved to memory.
* **Set Volume:** this allows to set the maximum volume that is available daily, in milliliters. Use up/down button to change, select/right to confirm, left to back.
* **Adjust syringe:** this allows you to manually move the motor, it is used when reloading a syringe.
* **Set piezo Thresh:** this allows you to set the sensitivity threshold for the piezoelectric element to trigger water delivery. It is set to 200 by default, it can be modified in increments of 5. After the initial setup, it should be calibrated in the following way: make sure both on and off timer as set at 00:00, and volume is set at 0 (this is ad libitum mode). Decrease the Piezo Thresh value in steps of 5, one step at a time, until continuous water delivery is triggered. Then, raise the Piezo Thresh by three/four 5-step above the value that trigger continuous delivery. When setting up a new unit, make sure to observe the mice long enough to see if they can easily trigger water delivery, without any false positive trigger.
* **Adjust Clock:** this option shows the current time. It can be manually adjusted, to compensate for clock drift or to implement daylight savings as appropriate.  

### Modes of operation
* **Ad libitum delivery:** both timers are set at 00:00, volume is set at 0. Water will be delivered every time a lick is detected.
* **Fixed time window availability:** volume is set at 0, timer on is set earlier than timer off. If current time is within timer on and timer off, water will be delivered when a lick is detected. Currently this window cannot go across days (i.e. you can set 17:30-21:45, but not 23:20-4:30).
* **Fixed volume:** timer on is set at the same time as timer off (i.e. 00:00-00:00, 4:00-4:00, 17:21-17:21). Volume is set at anything above 0. Water will be delivered when a lick is detected until the allowance is all used up. Current remaining allowance is shown in the default screen. Daily allowance is reset at time indicated by timer on and timer off (or when the device is reset/power cycled).
* **Hybrid:** timer on is set earlier than timer off, volume is set anything above 0. If current time is within timer on and timer off, water will be delivered unless the volume allowance has been used up. Daily allowance resets at the time indicated by timer on.

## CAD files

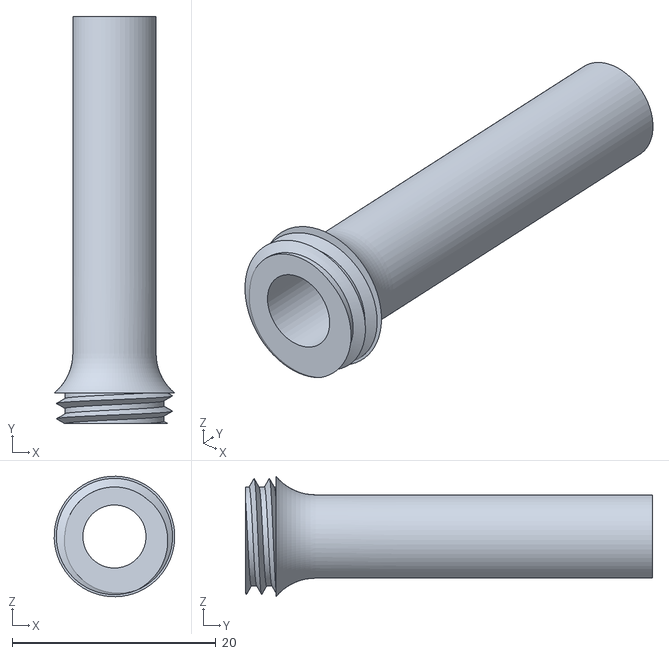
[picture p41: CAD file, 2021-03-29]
stl_parts/Spout_cover.stl
11.8 x 40.0 x 11.8

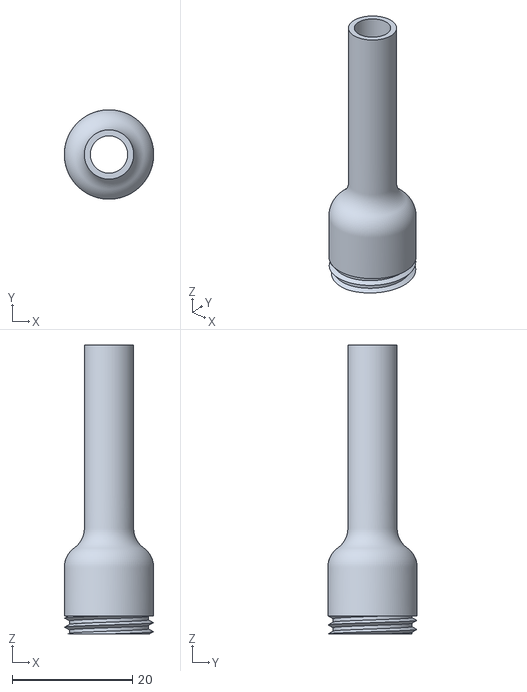
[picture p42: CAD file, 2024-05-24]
stl_parts/spout_v2/spout_v2.stl
14.8 x 14.8 x 48.0

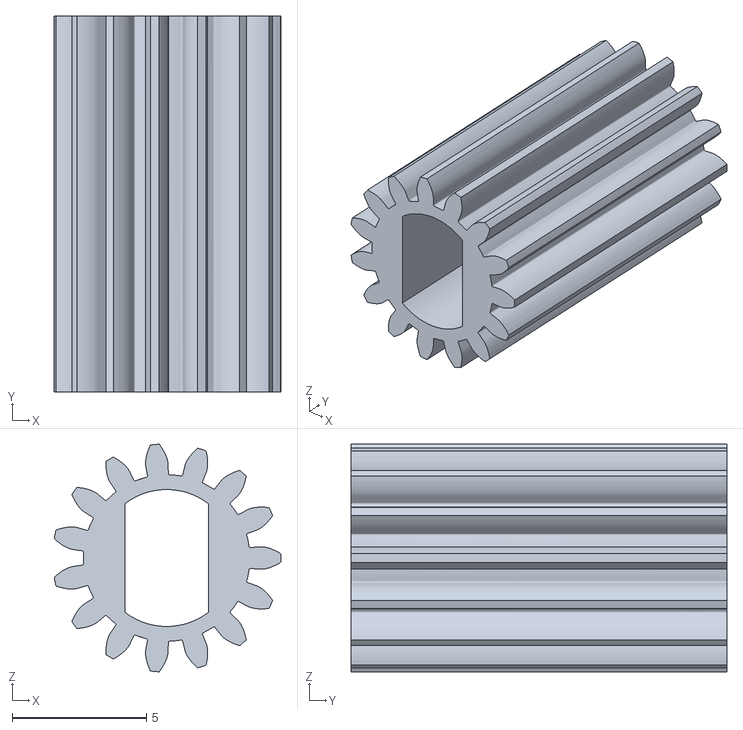
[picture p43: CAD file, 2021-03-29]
stl_parts/Pump_motor_pinion.stl
8.44 x 14.0 x 8.48

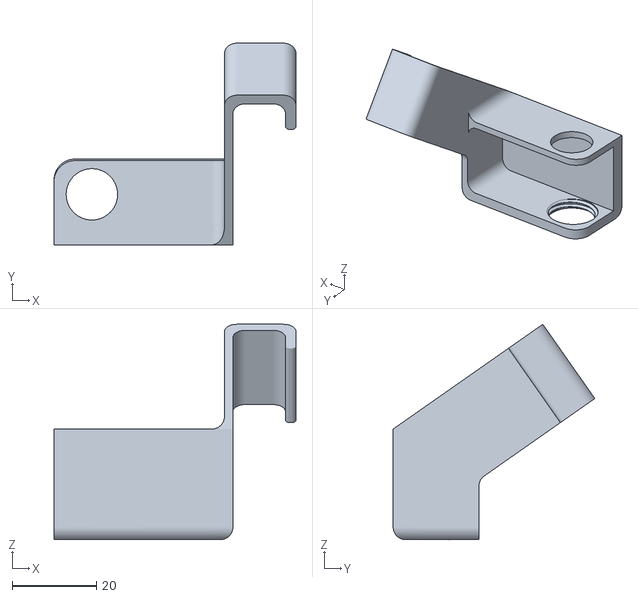
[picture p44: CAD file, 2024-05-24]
stl_parts/spout_v2/spoutholder_v2.stl
57.5 x 47.9 x 51.2

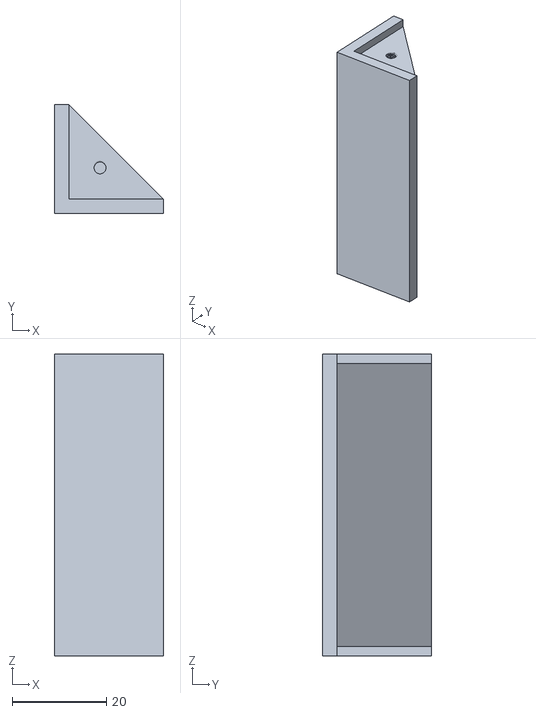
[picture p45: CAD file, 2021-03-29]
stl_parts/Corner_standoff.stl
23.0 x 23.0 x 64.0

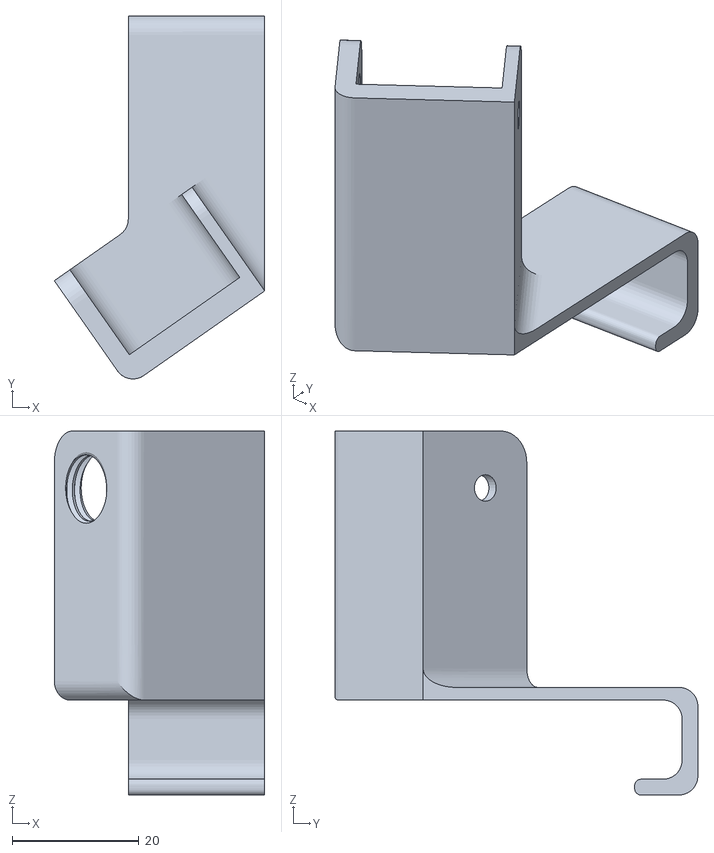
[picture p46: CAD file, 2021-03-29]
stl_parts/Spout_holder_opentop.stl
33.2 x 57.3 x 57.5

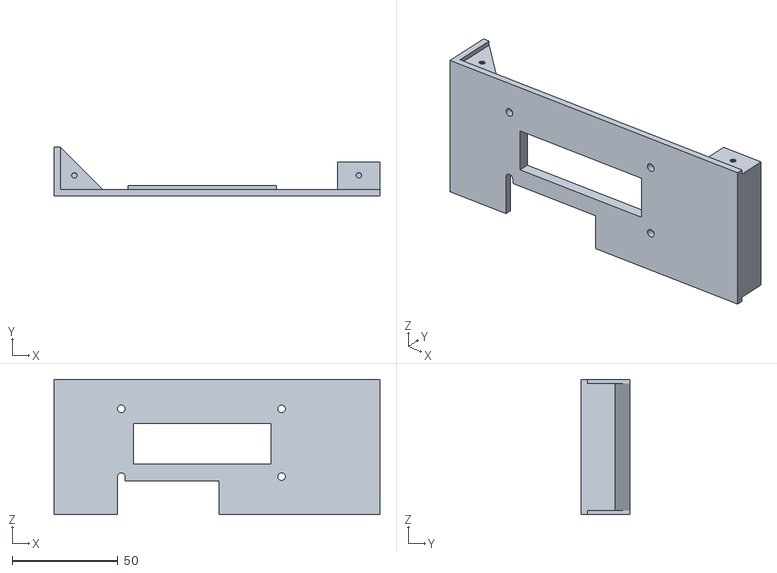
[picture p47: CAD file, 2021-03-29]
stl_parts/Front_panel.stl
154.0 x 23.0 x 64.0

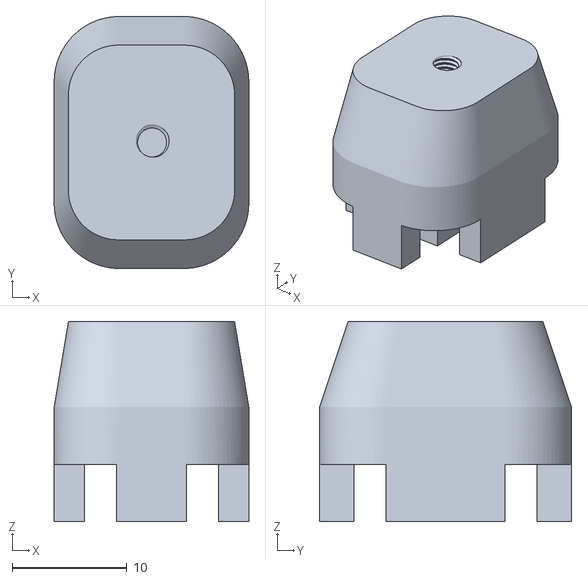
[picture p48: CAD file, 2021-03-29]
stl_parts/Foot.stl
17.0 x 22.0 x 17.5

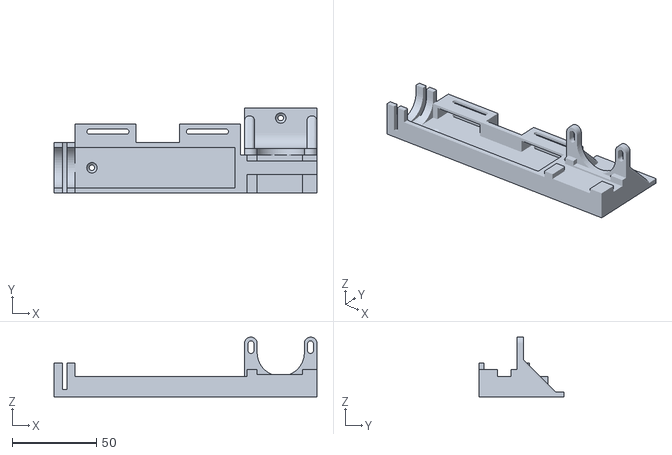
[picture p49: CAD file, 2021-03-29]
stl_parts/Pump_block.stl
156.0 x 50.5 x 35.5

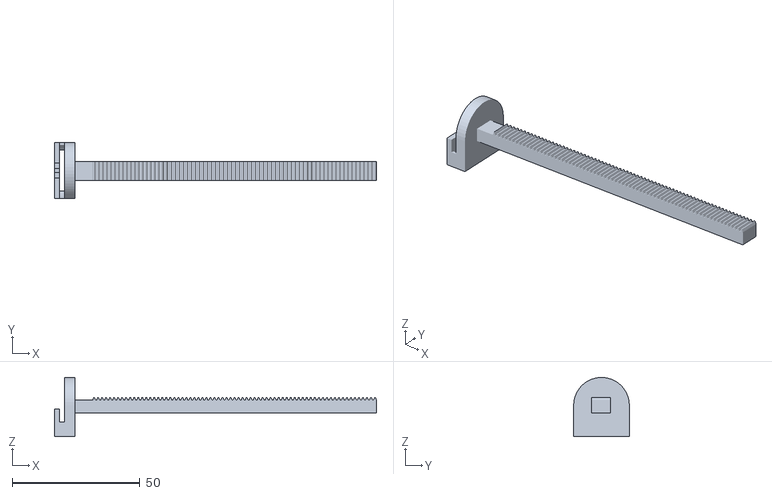
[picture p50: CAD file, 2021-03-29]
stl_parts/Pump_rack.stl
126.0 x 21.8 x 23.1

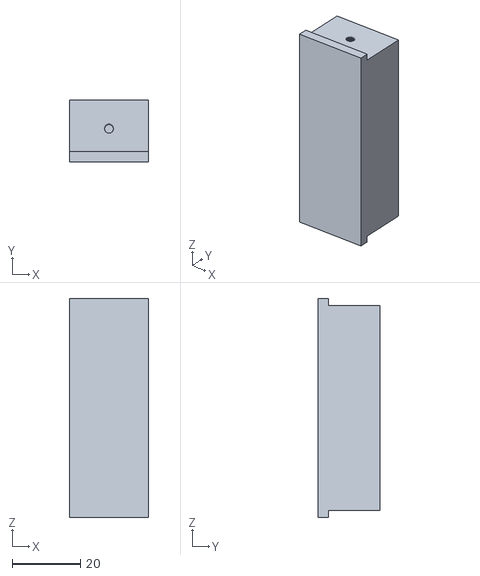
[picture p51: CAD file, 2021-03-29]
stl_parts/Flat_standoff.stl
23.0 x 18.0 x 64.0

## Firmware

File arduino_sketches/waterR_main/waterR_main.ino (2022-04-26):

/*
  WaterR is an open source device to control and monitor fluid intake in experimental rodents.
  Initially developed by Riccardo Avvisati at the University of Bristol in 2020

  Released under GNU GPLv3 License.
*/

#include <LiquidCrystal.h>
#include <SoftwareSerial.h>
#include <SdFat.h>
#include <StepperMotor.h>
#include <EEPROM.h>
#include <RTClib.h>
#include <SPI.h>

RTC_DS3231 rtc;
SdFatSoftSpi<12, 11, 13> sd;

SdFile logfile;
char filename[50];

StepperMotor motor(31, 33, 35, 37);         //initialize motor on in1, in2, in3, in4 pins

LiquidCrystal lcd(8, 9, 4, 5, 6, 7);    //initialize lcd screen (pins are fixed for the shield)

uint8_t volume;             //volume daily allowance in thents of ml (so that 1.5 ml is handled as 15) <- this is stored in EEPROM addres 4
uint8_t volume_;            //temp variable that is used to modify the volume value and overwrite it
float volumeLeft;           //variable to calculate volume left on allowance as floating point
float volumeDisplay;        //variable used to display volume as floating point for human reading
float volumeLeftDisplay;
float lastVolumeLeft = -1;

uint16_t deliveredUnits = 0;        //units of fluid delivered so far, initialize to zero
uint16_t deliveryUnits100ul = 7;    //coefficient used to convert volume to stepper motor steps based on syringe size
uint16_t lastAllowanceResetDay = 0;     //variable used to ensure that allowance is reset no more than once a day
uint16_t lastPrimingDay = 0;        //variable used to ensure that priming water delivery isn't given more than once a day
uint32_t lastWaterDeliveryTime = 0;

int8_t hourON;      //EEPROM address 0
int8_t minuteON;    //EEPROM address 1
int8_t hourOFF;     //EEPROM address 2
int8_t minuteOFF;   //EEPROM address 3
int8_t hourON_;     //temp variables for when the user is changing the timers
int8_t minuteON_;
int8_t hourOFF_;
int8_t minuteOFF_;

int8_t hourADJ;     //variables for manually adjusting the clock (too much drift, winter/summer time clock shift, etc.)
int8_t minuteADJ;
int8_t hourADJ_;
int8_t minuteADJ_;

uint8_t hourNOW;
uint8_t minuteNOW;
uint8_t dayNOW;
uint32_t unixtimeNOW;

uint16_t timestampNOW;    //timestamps
uint16_t timestampON;
uint16_t timestampOFF;

char volumeTem[5];        //char buffers for printf function
char timeONtem[10];
char timeOFFtem[10];
char hourONtem[3];
char minuteONtem[3];
char hourOFFtem[3];
char minuteOFFtem[3];
char piezoThreshTem[4];
char hourADJtem[3];
char minuteADJtem[3];
char timeADJtem[6];

uint8_t piezoPin = A8;      //pin connected to piezo sensor
uint8_t piezoGround = A9;   //pin that is pulled to ground to provide a "clean" ground for piezo sensor
int piezoThresh;            //threshold for lick detection, value is stored in eeprom
int piezoThresh_;           //temp var to hold user-modified piezo threshold value
uint32_t lastLickTime = 0;
uint32_t debounceLick = 1000;

uint8_t endSyringeStop = 25;
uint8_t endSyringeStopGround = 27;
uint8_t startSyringeStop = 100;

uint32_t lastInputTime = 0;
uint32_t debounce = 200;

uint16_t menuState = 0;
uint16_t lastMenuState = 1;

bool SDlogActive = false;
bool updateFlag = false;

//--------------------------------------------------------------- Functions

void stopMotor() {            //function that turns the motor off. Can be implemented if battery operation is required
  digitalWrite(31, LOW);
  digitalWrite(33, LOW);
  digitalWrite(35, LOW);
  digitalWrite(37, LOW);
}


int8_t readButtonPress() {                   //function that reads a button press based on A0 analog reading
  uint16_t buttonReading = analogRead(A0);

  if (buttonReading < 50) {
    return 4;
  }
  else if (buttonReading < 200) {
    return 1;
  }
  else if (buttonReading < 400) {
    return 2;
  }
  else if (buttonReading < 600) {
    return 3;
  }
  else if (buttonReading < 800 ) {
    return 0;
  }
  else {
    return -1;
  }
}


uint16_t readPiezoSignal() {
  uint16_t piezoRead = analogRead(piezoPin);

  //logfile.println(piezoRead);                 //debug lines, print the piezoRead value to SD
  //logfile.flush();                            //useful to check power supply noise on analog read

  return piezoRead;
}


void updateScreen() {                         //function that updates the screen when something changes (mostly because the user is navigating the menu and changing settings)
  if ((menuState != lastMenuState))  {

    switch (menuState) {
      case 0:
        lcd.clear();
        sprintf(timeONtem, "On  %02d:%02d", hourON, minuteON);
        sprintf(timeOFFtem, "Off %02d:%02d", hourOFF, minuteOFF);
        lcd.setCursor(0, 0);
        lcd.print(timeONtem);
        lcd.setCursor(0, 1);
        lcd.print(timeOFFtem);

        lcd.setCursor(13, 0);
        lcd.print("Vol");
        lcd.setCursor(13, 1);
        if (volume == 0) {
          lcd.print("N/A");
        }
        else {
          volumeLeftDisplay = float(volumeLeft) / 10;

          lcd.print(volumeLeftDisplay);
        }
        break;

      case 1:
        lcd.clear();
        lcd.setCursor(0, 0);
        lcd.print("Set Timer");
        break;
      case 2:
        lcd.clear();
        lcd.setCursor(0, 0);
        lcd.print("Set Volume");
        break;
      case 3:
        lcd.clear();
        lcd.setCursor(0, 0);
        lcd.print("Adjust Syringe");
        break;
      case 4:
        lcd.clear();
        lcd.setCursor(0, 0);
        lcd.print("Set piezo Threshold");
        break;
      case 5:
        { lcd.clear();
          DateTime now = rtc.now();
          sprintf(timeADJtem, "%02d:%02d", now.hour(), now.minute());
          lcd.setCursor(0, 0);
          lcd.print("Adjust Clock");
          lcd.setCursor(4, 1);
          lcd.print(timeADJtem);
          break;
        }
      case 11:
        if (lastMenuState == 1) {
          hourON_ = hourON;
          minuteON_ = minuteON;
          hourOFF_ = hourOFF;
          minuteOFF_ = minuteOFF;
        }

        lcd.clear();
        lcd.setCursor(0, 0);
        lcd.print("Time ON");
        lcd.setCursor(0, 1);
        lcd.print("Time OFF");

        sprintf(hourONtem, "%02d", hourON_);
        sprintf(minuteONtem, "%02d", minuteON_);
        sprintf(hourOFFtem, "%02d", hourOFF_);
        sprintf(minuteOFFtem, "%02d", minuteOFF_);

        lcd.setCursor(10, 0);
        lcd.print(hourONtem);
        lcd.print(":");
        lcd.print(minuteONtem);
        lcd.setCursor(10, 1);
        lcd.print(hourOFFtem);
        lcd.print(":");
        lcd.print(minuteOFFtem);

        lcd.setCursor(9, 0);
        lcd.print(">");
        break;
      case 12:
        lcd.setCursor(9, 0);
        lcd.print(" ");
        lcd.setCursor(9, 1);
        lcd.print(" ");

        lcd.setCursor(15, 0);
        lcd.print("<");
        break;
      case 13:
        lcd.setCursor(15, 0);
        lcd.print(" ");
        lcd.setCursor(15, 1);
        lcd.print(" ");

        lcd.setCursor(9, 1);
        lcd.print(">");
        break;
      case 14:
        lcd.setCursor(9, 1);
        lcd.print(" ");

        lcd.setCursor(15, 1);
        lcd.print("<");
        break;

      case 31:
        lcd.clear();
        lcd.setCursor(0, 0);
        lcd.print("Move Syringe w/");
        lcd.setCursor(0, 1);
        lcd.print("Up/Down buttons");
        break;

      case 21:
        volume_ = volume;
        volumeDisplay = float(volume_) / 10;

        lcd.clear();
        lcd.setCursor(0, 0);
        lcd.print("Volume: ");
        lcd.setCursor(8, 0);
        lcd.print(volumeDisplay);
        lcd.setCursor(13, 0);
        lcd.print("ml");
        break;

      case 41:
        piezoThresh_ = piezoThresh;
        lcd.clear();
        lcd.setCursor(0, 0);
        lcd.print("Thresh for lick:");
        lcd.setCursor(0, 1);
        lcd.print(piezoThresh_);
        break;

      case 51:
        if (lastMenuState == 5) {
          DateTime now = rtc.now();
          hourADJ_ = now.hour();
          minuteADJ_ = now.minute();
        }
        sprintf(hourADJtem, "%02d", hourADJ_);
        sprintf(minuteADJtem, "%02d", minuteADJ_);

        lcd.clear();
        lcd.setCursor(0, 0);
        lcd.print("Set current time");
        lcd.setCursor(4, 1);
        lcd.print(hourADJtem);
        lcd.print(":");
        lcd.print(minuteADJtem);

        lcd.setCursor(3, 1);
        lcd.print(">");
        break;

      case 52:
        lcd.setCursor(3, 1);
        lcd.print(" ");
        lcd.setCursor(9, 1);
        lcd.print("<");
        break;
    }
    lastMenuState = menuState;
  }
  else if (updateFlag) {
    switch (menuState) {
      case 11:
        sprintf(hourONtem, "%02d", hourON_);
        lcd.setCursor(10, 0);
        lcd.print(hourONtem);
        break;
      case 12:
        sprintf(minuteONtem, "%02d", minuteON_);
        lcd.setCursor(13, 0);
        lcd.print(minuteONtem);
        break;
      case 13:
        sprintf(hourOFFtem, "%02d", hourOFF_);
        lcd.setCursor(10, 1);
        lcd.print(hourOFFtem);
        break;
      case 14:
        sprintf(minuteOFFtem, "%02d", minuteOFF_);
        lcd.setCursor(13, 1);
        lcd.print(minuteOFFtem);
        break;

      case 21:
        volumeDisplay = float(volume_) / 10;
        lcd.setCursor(8, 0);
        lcd.print(volumeDisplay);
        break;

      case 41:
        sprintf(piezoThreshTem, "%3d", piezoThresh_);
        lcd.setCursor(0, 1);
        lcd.print(piezoThreshTem);
        break;

      case 51:
        sprintf(hourADJtem, "%02d", hourADJ_);
        lcd.setCursor(4, 1);
        lcd.print(hourADJtem);
        break;

      case 52:
        sprintf(minuteADJtem, "%02d", minuteADJ_);
        lcd.setCursor(7, 1);
        lcd.print(minuteADJtem);
        break;

      case 0:
        volumeLeftDisplay = float(volumeLeft) / 10;
        lcd.setCursor(13, 1);
        if ((volume != 0) && (volumeLeft >= 0)) {
          lcd.print(volumeLeftDisplay);
        }
        else if (volume == 0) {
          lcd.print("N/A");
        }
        break;
    }
    updateFlag = false;
  }
}
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

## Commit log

2022-01-27 updated assembly instructions
2022-04-26 water volume left is not reset between power cycles anymore
2024-05-23 added new version of the lickspout to make it slightly wider
    [spout_v2.stl, spoutholder_v2.stl]
2024-05-24 updated models to add more clearence for screw
    [spout_v2.stl, spoutholder_v2.stl]
